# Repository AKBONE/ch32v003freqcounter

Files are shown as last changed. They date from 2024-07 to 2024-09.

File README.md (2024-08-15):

# ch32v003freqcounter

This is an electronic construction kit teaching material for kids' science experiment classes.
## Sound learning

It takes in sound, counts the frequencies, and displays them.

Learn what frequency various sounds are,
You can learn how the Doppler effect is generated by motion to a sound source.

In the future, the system will be able to display waveforms, measure ultrasonic frequencies, and output sounds of arbitrary frequencies.
This will allow students to learn that sound is a wave, that sounds are not audible to humans, and that different sounds can be heard at different ages.

## Concept
We try to make the kit as inexpensive as possible. We try to make the kit as inexpensive as possible and use inexpensive microcontrollers for this purpose.

## Soldering Training
The main components are soldered at the factory during manufacturing. The remaining few through-hole parts are made to be completed by soldering.

## Applications

With its small footprint and fast screen display, it can be used as a small signage.

# Circuit

## Schematic



## artdesign


# pin assign

| CH32V003F4P6 PIN |           | OLED PIN | OLED |
|------------------|-----------|----------|------|
|                  |           | 1        | GND  |
|                  |           | 2        | 3.3V |
| 15               |           | 3        | D0   |
| 16               | MOSI       | 4        | D1   |
| 17               | PC7(MISO) | 5        | RST  |
| 14               | PC4      | 6        | DC   |
| 13               | PC3       | 7        | CS   |

| CH32V003F4P6 PIN |       | PROGRAM PIN |   | LED(D1) |         |
|------------------|-------|-------------|-------|---------|---------|
|                  |       | 1           | 3.3V  |         |         |
| 18               | SWDIO | 2           | SWDIO |         |         |
|                  |       | 3           | GND   |         | CATHODE |
| 4                | NRST  | 4           | RST   |         |         |
| 2                | UTX   | 5           | TX    |         | ANODE   |
| 3                | URX   | 6           | RX    |         |         |

| CH32V003F4P6 PIN |           | SW  |  |
|------------------|-----------|-----|------|
| 8                | PD0       | SW1 | OK   |
| 10               | PC0       | SW2 | ↓    |
| 1                | PD4       | SW3 | ↑    |

| CH32V003F4P6 PIN |         | SEEED_GROVE |    |
|------------------|---------|-------------|--------|
| 12               | PC2/SCL | 1           | YELLOW |
| 11               | PC1/SDA | 2           | WHITE  |
|                  |         | 3           | 3.3V   |
|                  |         | 4           | GND    |

| CH32V003F4P6 PIN |        | NAX4466_MIC_MODULE |  |
|------------------|--------|--------------------|------|
| 20               | PD3/A4 | 1                  | OUT  |
|                  |        | 2                  | GND  |
|                  |        | 3                  | 3.3V |

| CH32V003F4P6 PIN |      | SPEAKER |  |
|------------------|------|---------|------|
|                  |      | 1       | GND  |
| 19               | PD2  | 2       | IN   |

## Links
- [ユーザ向けポータルサイト](https://akbone.github.io/ch32v003freqcounter/)
- [50円マイコン ch32v003 を使った簡単キット(AKBONE2024)を組み立てる #RISC-V - Qiita](https://qiita.com/nanbuwks/items/22680849ee7674d66a89)

### For Engineer
- [AKBONE/ch32v003freqcounter](https://github.com/AKBONE/ch32v003freqcounter)
- [cnlohr/ch32v003fun: Open source minimal stack for the ch32 line of WCH processors, including the ch32v003, a 10¢ 48 MHz RISC-V Microcontroller - as well as many other chips within the ch32v/x line.](https://github.com/cnlohr/ch32v003fun)

#### Parts
- [32ビットRISC-Vマイコン CH32V003F4P6: 半導体 秋月電子通商-電子部品・ネット通販](https://akizukidenshi.com/catalog/g/g118061/)
  - [データシート](https://akizukidenshi.com/goodsaffix/CH32V003.pdf)

# License

Public Domain ((cc0)
However, libraries used are subject to individual licenses.

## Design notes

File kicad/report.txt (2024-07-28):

情報: ファイル '/home/nanbuwks/00storage/KiCad/FreqCounter3203/github/kicad/sym-lib-table' をファイル '/home/nanbuwks/00storage/KiCad/FreqCounter3203/github/kicad/rescue-backup/sym-lib-table-2024-07-25-21-31-20' にバックアップしています。
情報: ファイル '/home/nanbuwks/00storage/KiCad/FreqCounter3203/github/kicad/FreqCounter3203.sch' をファイル '/home/nanbuwks/00storage/KiCad/FreqCounter3203/github/kicad/rescue-backup/FreqCounter3203-2024-07-25-21-31-20.sch' にバックアップしています。
情報: ファイル '/home/nanbuwks/00storage/KiCad/FreqCounter3203/github/kicad/FreqCounter3203.kicad_pro' をファイル '/home/nanbuwks/00storage/KiCad/FreqCounter3203/github/kicad/rescue-backup/FreqCounter3203-2024-07-25-21-31-20.kicad_pro' にバックアップしています。
情報: ファイル '/home/nanbuwks/00storage/KiCad/FreqCounter3203/github/kicad/FreqCounter3203-cache.lib' をファイル '/home/nanbuwks/00storage/KiCad/FreqCounter3203/github/kicad/rescue-backup/FreqCounter3203-cache-2024-07-25-21-31-20.lib' にバックアップしています。
情報: ファイル '/home/nanbuwks/00storage/KiCad/FreqCounter3203/github/kicad/FreqCounter3203-rescue.lib' をファイル '/home/nanbuwks/00storage/KiCad/FreqCounter3203/github/kicad/rescue-backup/FreqCounter3203-rescue-2024-07-25-21-31-20.lib' にバックアップしています。
情報: ファイル '/home/nanbuwks/00storage/KiCad/FreqCounter3203/github/kicad/FreqCounter3203-rescue.dcm' をファイル '/home/nanbuwks/00storage/KiCad/FreqCounter3203/github/kicad/rescue-backup/FreqCounter3203-rescue-2024-07-25-21-31-20.dcm' にバックアップしています。
情報: ライブラリ 'FreqCounter3203-rescue' , ファイル '${KIPRJMOD}/FreqCounter3203-rescue.lib' をプロジェクトのシンボル ライブラリ テーブルへ追加します。
シンボル 'CONN_01X06' はシンボル ライブラリ 'FreqCounter3203-rescue' にマップされました。
シンボル 'DIODESCH' はシンボル ライブラリ 'FreqCounter3203-rescue' にマップされました。
シンボル 'SWITCH_INV' はシンボル ライブラリ 'FreqCounter3203-rescue' にマップされました。
シンボル 'Battery' はシンボル ライブラリ 'FreqCounter3203-rescue' にマップされました。
シンボル 'CONN_02X03' はシンボル ライブラリ 'FreqCounter3203-rescue' にマップされました。
シンボル 'Battery' はシンボル ライブラリ 'FreqCounter3203-rescue' にマップされました。
シンボル 'SW_PUSH' はシンボル ライブラリ 'FreqCounter3203-rescue' にマップされました。
シンボル 'SW_PUSH' はシンボル ライブラリ 'FreqCounter3203-rescue' にマップされました。
シンボル 'C' はシンボル ライブラリ 'FreqCounter3203-rescue' にマップされました。
シンボル 'PhotoReciever_GP1USC4XQS_SHARP' はシンボル ライブラリ 'FreqCounter3203-rescue' にマップされました。
シンボル 'GND' はシンボル ライブラリ 'FreqCounter3203-rescue' にマップされました。
シンボル 'R' はシンボル ライブラリ 'FreqCounter3203-rescue' にマップされました。
シンボル 'SW_PUSH' はシンボル ライブラリ 'FreqCounter3203-rescue' にマップされました。
シンボル 'SW_PUSH' はシンボル ライブラリ 'FreqCounter3203-rescue' にマップされました。
シンボル '+3.3V' はシンボル ライブラリ 'FreqCounter3203-rescue' にマップされました。
シンボル 'R' はシンボル ライブラリ 'FreqCounter3203-rescue' にマップされました。
シンボル 'GND' はシンボル ライブラリ 'FreqCounter3203-rescue' にマップされました。
シンボル 'GND' はシンボル ライブラリ 'FreqCounter3203-rescue' にマップされました。
シンボル '+3.3V' はシンボル ライブラリ 'FreqCounter3203-rescue' にマップされました。
シンボル 'STM32F103C8T6MinimumDevelopBoard-RESCUE-nodrinknohack' はシンボル ライブラリ 'FreqCounter3203-rescue' にマップされました。
シンボル 'SPEAKER' はシンボル ライブラリ 'FreqCounter3203-rescue' にマップされました。
シンボル 'GND' はシンボル ライブラリ 'FreqCounter3203-rescue' にマップされました。
シンボル 'SW_PUSH' はシンボル ライブラリ 'FreqCounter3203-rescue' にマップされました。
シンボル 'GND' はシンボル ライブラリ 'FreqCounter3203-rescue' にマップされました。
シンボル '+3.3V' はシンボル ライブラリ 'FreqCounter3203-rescue' にマップされました。
シンボル 'OLED_0.96in_SPI' はシンボル ライブラリ 'FreqCounter3203-rescue' にマップされました。
シンボル 'R' はシンボル ライブラリ 'FreqCounter3203-rescue' にマップされました。
シンボル 'LED' はシンボル ライブラリ 'FreqCounter3203-rescue' にマップされました。
シンボル 'GND' はシンボル ライブラリ 'FreqCounter3203-rescue' にマップされました。
シンボル 'SW_PUSH' はシンボル ライブラリ 'FreqCounter3203-rescue' にマップされました。
シンボル 'R' はシンボル ライブラリ 'FreqCounter3203-rescue' にマップされました。
シンボル '+3.3V' はシンボル ライブラリ 'FreqCounter3203-rescue' にマップされました。
情報: シンボル ライブラリ テーブルのマッピングを完了!
情報: プロジェクトのシンボル ライブラリ テーブルを作成しました。

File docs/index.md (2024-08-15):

# AKBONE2024 (ch32v003freqcounter)

「おとカウンター」キットのページです。
いろんなイベントで頒布しています。

## 教科書

最新の教科書はこちら
-  [textbook](./text/textbook.pdf) 

過去の教科書は「イベント」内のリンクを参照してください。

## こんなときは

### 使い方を知りたい

「イベント」内に、イベントで頒布したキットの説明書のリンクがあります。説明書で確認してください。

### こわれちゃったよ!

「OpenHardTerrace」という Discord サーバでサポートしています。

[https://discord.gg/9UTNdtSrdX](https://discord.gg/9UTNdtSrdXa)

こちらに参加後、ご連絡ください。

あらかじめ、 Discord のアカウントの用意が必要です。 
ご参加後、 「PROJECTS」 →  「akbone2024」 に行き、いつどこで入手したかと症状を書いてください。

Discord へのアクセスが難しい場合は、以下の住所まではがきでご連絡ください。

〒297-0037 千葉県茂原市早野2756-2
秘密結社オープンフォース 秘密基地

### より知りたいとき

技術的な設計情報などは、 GitHub で管理しています。
[https://github.com/AKBONE/ch32v003freqcounter](https://github.com/AKBONE/ch32v003freqcounter)
また、「こわれちゃったよ」と同じ Discord サーバーで開発をしています。興味があればご参加ください。

## イベント
- 2024/08/04 [なつやすみこども科学実験教室2024](./events/2024-08-04/) @東京都足立区伊興地域学習センター [https://openforce.connpass.com/event/326569/](https://openforce.connpass.com/event/326569/)
- 2024/08/10 [なつやすみこども科学実験教室2024](./events/2024-08-10-11/) @石川県七尾市和倉地区コミュニティセンター
- 2024/08/11 [なつやすみ科学実験教室2024](./events/2024-08-10-11/) @石川県珠洲市旧正院保育所

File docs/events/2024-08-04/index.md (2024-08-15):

# 2024-08-04

東京都足立区伊興コミュニティセンターで開催した科学実験教室内で「おとカウンターをはんだづけしてみよう！」コーナーとして頒布しました。

## 説明書
[https://docs.google.com/document/d/1sSZhSKSC-4plJ0KE5L4aG0ssfCy5kGWXfLFpL6DbHqM/](https://docs.google.com/document/d/1sSZhSKSC-4plJ0KE5L4aG0ssfCy5kGWXfLFpL6DbHqM/)
## イベントサイト 
- [なつやすみこども科学実験教室2024 - connpass](https://openforce.connpass.com/event/326569/)

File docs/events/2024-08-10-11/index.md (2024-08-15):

# 2024/08/10-11

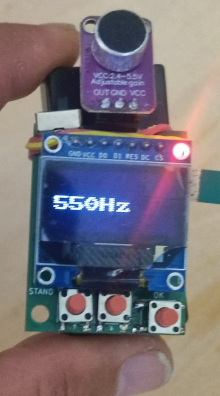
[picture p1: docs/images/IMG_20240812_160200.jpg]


## 開催

### 2024/08/10

- 2024/08/10 なつやすみこども科学実験教室2024 @石川県七尾市和倉地区コミュニティセンター
- 2024/08/11 なつやすみ科学実験教室2024 @石川県珠洲市旧正院保育所

## テキストブック
-  [textbook](./text/textbook.pdf)

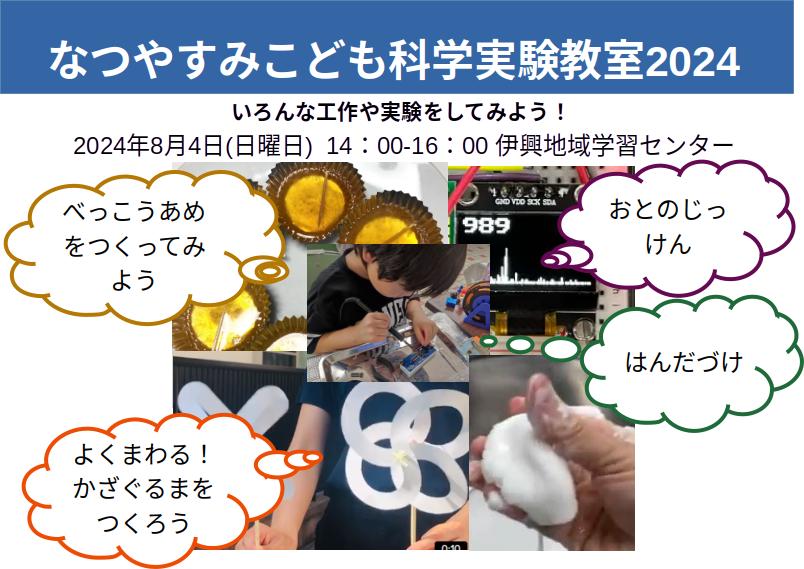
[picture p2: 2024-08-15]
pictures/leaflets.jpg

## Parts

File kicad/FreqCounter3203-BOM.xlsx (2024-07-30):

Comment | Designator | Footprint
2.7kΩ | R2 | R_0603_1608Metric | C13167
47 | R9,R8 | R_0603_1608Metric | C23179
1u | C6 | C_0603_1608Metric | C59302
20p | C2,C3 | C_0603_1608Metric | C165732
10u | C4,C5 | C_0603_1608Metric | C38898
0.1u | C1 | C_0603_1608Metric | C14663
XC6206PxxxMR | U4 | SOT-23-3 | C5446
5.1k | R5,R6 | R_0603_1608Metric | c23186
TACTSWWITCH | SW1,SW2,SW3 | SW_Push_1P1T_NO_6x6mm_H9.5mm | c2837533
180Ω | R1 | R_0603_1608Metric | c22828
CH32V003F4P6 | U3 | TSSOP-20_4.4x6.5mm_P0.65mm | c5187096
1.5k | R7 | R_0603_1608Metric | c22843
USB-C_16PIN | U5 | USB_Type_C_16Pin_Female | c393939
Battery | BT1 | BatteryHolder_Keystone_3002_1x2032 | c964834
LED | D1 | LED_D3.0mm | C2895470
SEEED_GROVE | U1 | JST_PH_B4B-PH-K_1x04_P2.00mm_Vertical | C722737

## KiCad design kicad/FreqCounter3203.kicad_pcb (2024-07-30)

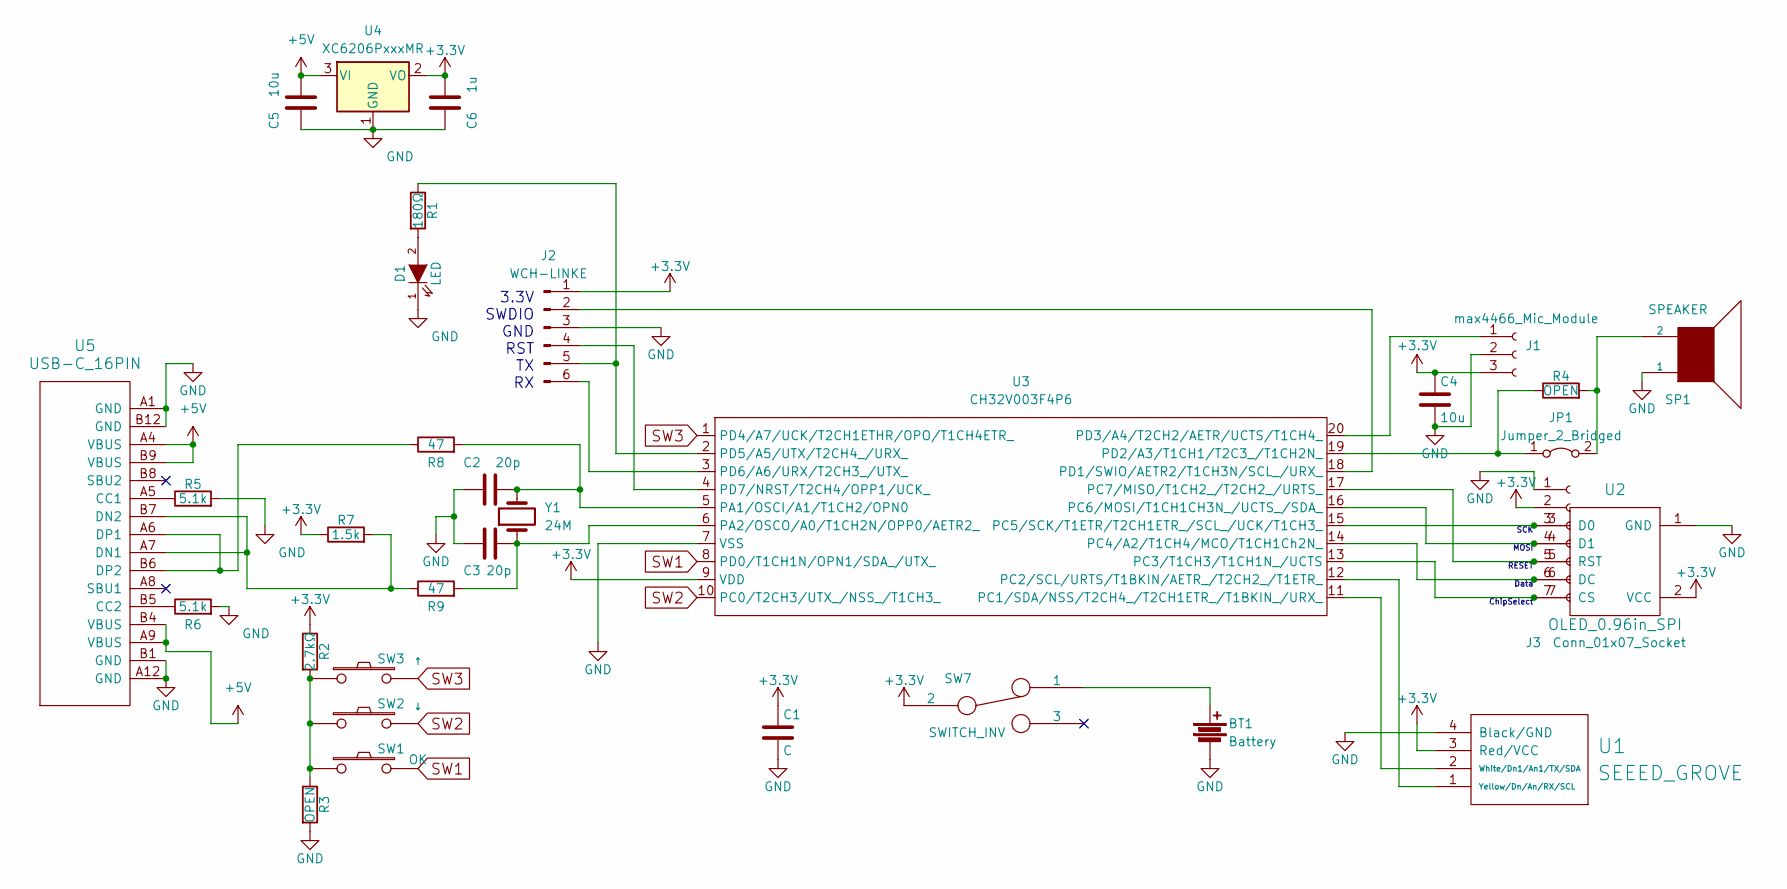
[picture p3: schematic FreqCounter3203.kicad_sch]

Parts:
BT1: Battery; BatteryHolder_Keystone_3002_1x2032
C1: C; C_0603_1608Metric
C2, C3: 20p; C_0603_1608Metric
C4, C5: 10u; C_0603_1608Metric
C6: 1u; C_0603_1608Metric
D1: LED; LED_D3.0mm
J1: max4466_Mic_Module; PinHeader_1x03_P2.54mm_Vertical
J2: WCH-LINKE; PinHeader_1x06_P2.54mm_Vertical
J3: Conn_01x07_Socket; PinSocket_1x07_P2.54mm_Vertical
JP1: Jumper_2_Bridged; SolderJumper-2_P1.3mm_Bridged_Pad1.0x1.5mm
R1: 180Ω; R_0603_1608Metric
R2: 2.7kΩ; R_0603_1608Metric
R3, R4: OPEN; R_0603_1608Metric
R5, R6: 5.1k; R_0603_1608Metric
R7: 1.5k; R_0603_1608Metric
R8, R9: 47; R_0603_1608Metric
SP1: SPEAKER; Buzzer_TDK_PS1240P02BT_D12.2mm_H6.5mm
SW1: OK; SW_Push_1P1T_NO_6x6mm_H9.5mm
SW2: ↓; SW_Push_1P1T_NO_6x6mm_H9.5mm
SW3: ↑; SW_Push_1P1T_NO_6x6mm_H9.5mm
SW7: SWITCH_INV; PinHeader_1x03_P2.54mm_Vertical
U1: SEEED_GROVE; JST_PH_B4B-PH-K_1x04_P2.00mm_Vertical
U2: OLED_0.96in_SPI
U3: CH32V003F4P6; TSSOP-20_4.4x6.5mm_P0.65mm
U4: XC6206PxxxMR; SOT-23-3
U5: USB-C_16PIN; USB_Type_C_16Pin_Female
Y1: 24M; Crystal_SMD_HC49-SD

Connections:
+3V3: C1.1, C4.1, C6.2, J1.3, J2.1, J3.2, R2.1, R7.1, SW7.2, U1.3 (Red/VCC), U2.2 (VCC), U3.9 (VDD), U4.2 (VO)
+5V: C5.2, U4.3 (VI), U5.A4 (VBUS), U5.A9 (VBUS), U5.B4 (VBUS), U5.B9 (VBUS)
GND: BT1.2, C1.2, C2.1, C3.1, C4.2, C5.1, C6.1, D1.1 (K), J1.2, J2.3, J3.1, R3.2, R5.2, R6.2, SP1.1, U1.4 (Black/GND), U2.1 (GND), U3.7 (VSS), U4.1 (GND), U5.A1 (GND), U5.A12 (GND), U5.B1 (GND), U5.B12 (GND)
unnamed: BT1.1, SW7.1
unnamed: D1.2 (A), R1.2
unnamed: J1.1, U3.20 (PD3/A4/T2CH2/AETR/UCTS/T1CH4_)
unnamed: J2.2, U3.18 (PD1/SWIO/AETR2/T1CH3N/SCL_/URX_)
unnamed: J2.4, U3.4 (PD7/NRST/T2CH4/OPP1/UCK_)
unnamed: J2.5, R1.1, U3.2 (PD5/A5/UTX/T2CH4_/URX_)
unnamed: J2.6, U3.3 (PD6/A6/URX/T2CH3_/UTX_)
unnamed: J3.3, U2.3 (D0), U3.15 (PC5/SCK/T1ETR/T2CH1ETR_/SCL_/UCK/T1CH3_)
unnamed: J3.4, U2.4 (D1), U3.16 (PC6/MOSI/T1CH1CH3N_/UCTS_/SDA_)
unnamed: J3.5, U2.5 (RST), U3.17 (PC7/MISO/T1CH2_/T2CH2_/URTS_)
unnamed: J3.6, U2.6 (DC), U3.14 (PC4/A2/T1CH4/MCO/T1CH1Ch2N_)
unnamed: J3.7, U2.7 (CS), U3.13 (PC3/T1CH3/T1CH1N_/UCTS)
unnamed: JP1.1 (A), R4.1, U3.19 (PD2/A3/T1CH1/T2C3_/T1CH2N_)
unnamed: JP1.2 (B), R4.2, SP1.2
unnamed: R2.2, R3.1, SW1.1, SW2.1, SW3.1
unnamed: U1.2 (White/Dn1/An1/TX/SDA), U3.11 (PC1/SDA/NSS/T2CH4_/T2CH1ETR_/T1BKIN_/UR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)
unnamed: U1.1 (Yellow/Dn/An/RX/SCL), U3.12 (PC2/SCL/URTS/T1BKIN/AETR_/T2CH2_/T1ETR_)
unnamed: C2.2, R8.2, U3.5 (PA1/OSCI/A1/T1CH2/OPN0), Y1.2
unnamed: C3.2, R9.2, U3.6 (PA2/OSCO/A0/T1CH2N/OPP0/AETR2_), Y1.1
unnamed: R5.1, U5.A5 (CC1)
unnamed: R6.1, U5.B5 (CC2)
unnamed: R7.2, R9.1, U5.A7 (DN1), U5.B7 (DN2)
unnamed: R8.1, U5.A6 (DP1), U5.B6 (DP2)
SW1: SW1.2, U3.8 (PD0/T1CH1N/OPN1/SDA_/UTX_)
SW2: SW2.2, U3.10 (PC0/T2CH3/UTX_/NSS_/T1CH3_)
SW3: SW3.2, U3.1 (PD4/A7/UCK/T2CH1ETHR/OPO/T1CH4ETR_)

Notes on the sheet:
3.3V SWDIO GND RST TX RX
SCK MOSI RESET Data ChipSelect

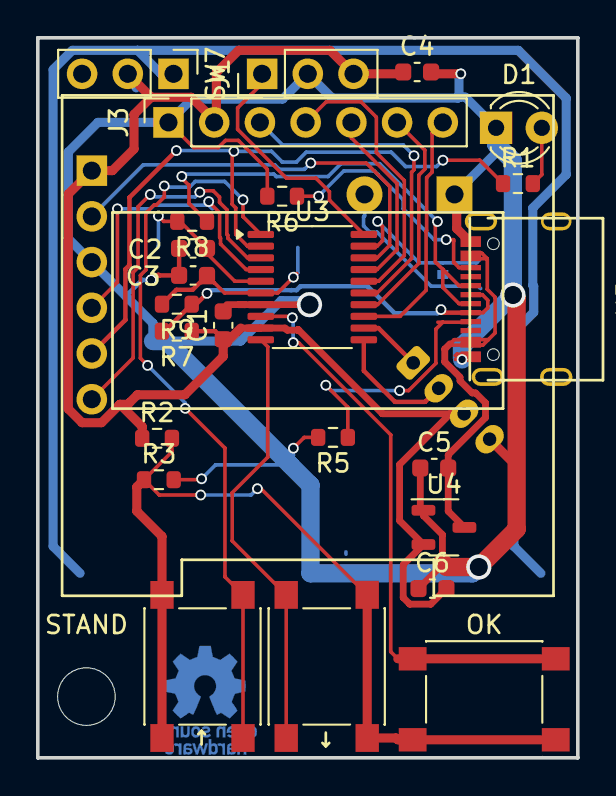
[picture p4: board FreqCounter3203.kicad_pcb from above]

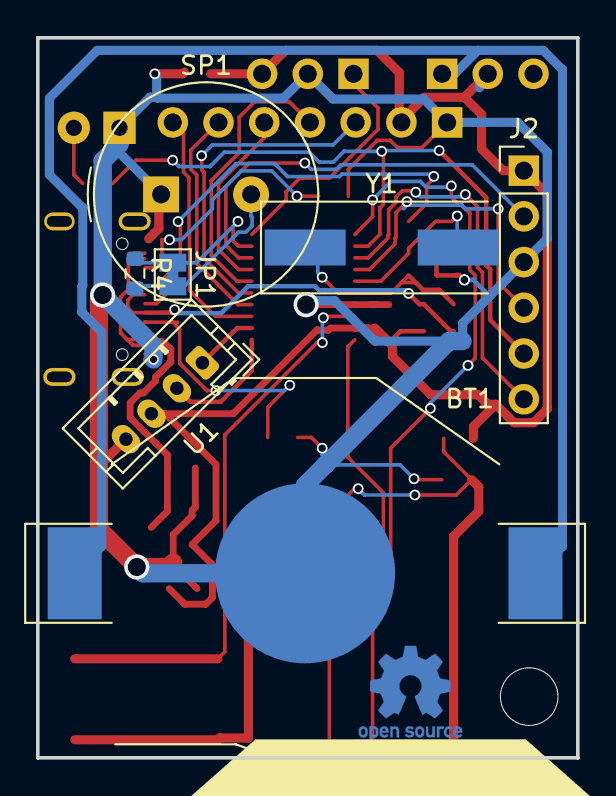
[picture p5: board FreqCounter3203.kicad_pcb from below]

Board: 2 copper layers, 30.0 x 40.0 mm, 32 parts (7 on the bottom side), 29 nets.

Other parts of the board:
STAND: MountingHole_3mm

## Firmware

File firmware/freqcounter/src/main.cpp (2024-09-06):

//
//	freqcounter Ver 1.1.1
//
//  2024.07.31 New Create
//
#include <stdio.h>
#include <stdlib.h> 
#include <math.h>
#include "fix_fft.h"
#include "ch32v003fun.h"

#define micros() (SysTick->CNT / DELAY_US_TIME)
#define millis() (SysTick->CNT / DELAY_MS_TIME)

// what type of OLED - uncomment just one
//#define SSD1306_64X32
//#define SSD1306_128X32
#define SSD1306_128X64
#define SCALE 3

#define GPIO_ADC_MUX_DELAY 100
#define GPIO_ADC_sampletime GPIO_ADC_sampletime_43cy
#include "ch32v003_GPIO_branchless.h"
#include "ssd1306_spi.h"
#include "ssd1306.h"

#define LED_PIN GPIOv_from_PORT_PIN(GPIO_port_D, 5)
#define SW1_PIN GPIOv_from_PORT_PIN(GPIO_port_D, 0)
#define SW2_PIN GPIOv_from_PORT_PIN(GPIO_port_D, 4)
#define SW3_PIN GPIOv_from_PORT_PIN(GPIO_port_C, 0)
#define ADC_PIN GPIOv_from_PORT_PIN(GPIO_port_D, 3)
#define SPK_PIN GPIOv_from_PORT_PIN(GPIO_port_D, 2)

#define SAMPLES 256 // 2の累乗である必要があります
#define SAMPLING_FREQUENCY 6000

uint16_t sampling_period_us;
int8_t vReal[SAMPLES];
int8_t vImag[SAMPLES];

#include "qr.h"

// function prototype (declaration), definition in "ch32v003fun.c"
extern "C" int mini_snprintf(char* buffer, unsigned int buffer_len, const char *fmt, ...);
char title1[] = "FrequencyCounter";
char title2[] = "  Version 1.1.1 ";


void setup()
{
    // 各GPIOの有効化
    GPIO_port_enable(GPIO_port_D);
    GPIO_port_enable(GPIO_port_C);
    // 各ピンの設定
    GPIO_pinMode(SW1_PIN, GPIO_pinMode_I_pullDown, GPIO_Speed_10MHz); /// GPIO_Speed_In? @see https://github.com/cnlohr/ch32v003fun/blob/master/examples/GPIO/GPIO.c#L55
    GPIO_pinMode(SW2_PIN, GPIO_pinMode_I_pullDown, GPIO_Speed_10MHz);
    GPIO_pinMode(SW3_PIN, GPIO_pinMode_I_pullDown, GPIO_Speed_10MHz);

	ssd1306_spi_init();		// i2c Setup
	ssd1306_init();			// SSD1306 Setup
	ssd1306_setbuf(0);		// Clear Screen
	ssd1306_drawstr_sz(0, 24, title1, 1, fontsize_8x8);
	ssd1306_drawstr_sz(0, 40, title2, 1, fontsize_8x8);
	ssd1306_refresh();
}

// void alertNotImpl() {
// 	ssd1306_setbuf(0);		// Clear Screen
// 	ssd1306_drawstr_sz(0, 24, "      Not       ", 1, fontsize_8x8);
// 	ssd1306_drawstr_sz(0, 40, "  Implemented!  ", 1, fontsize_8x8);
// 	ssd1306_refresh();
// 	Delay_Ms(1000);
// }

// void alertDefaultError() {
// 	ssd1306_setbuf(0);		// Clear Screen
// 	ssd1306_drawstr_sz(0, 24, "some error occurrs", 1, fontsize_8x8);
// 	ssd1306_drawstr_sz(0, 40, "    Reboot Me!    ", 1, fontsize_8x8);
// 	ssd1306_refresh();
// 	while(1);
// }

void drawIcon(uint8_t *data, uint8_t size, uint8_t x_base, uint8_t y_base, uint8_t color) {
	for (uint8_t i = 0; i < size; i++) {
		for (uint8_t j = 0; j < size; j++) {
			uint8_t pixel = *(data + i * size + j);
			bool _color = (color && pixel) || (!color && !pixel);
			ssd1306_drawPixel(x_base + j, y_base + i, _color);
		}
	}
}

void drawWaveIcon0(uint8_t x_base, uint8_t y_base, uint8_t color) {
	uint8_t data[8][8] = {
		{0, 0, 0, 0, 1, 0, 0, 0},
		{0, 0, 0, 1, 0, 1, 0, 0},
		{0, 0, 1, 0, 0, 0, 1, 0},
		{0, 0, 1, 0, 0, 0, 1, 0},
		{0, 1, 0, 0, 0, 0, 0, 1},
		{0, 1, 0, 0, 0, 0, 0, 1},
		{1, 0, 0, 0, 0, 0, 0, 0},
		{1, 0, 0, 0, 0, 0, 0, 0},
	};

	drawIcon((uint8_t*) data, 8, x_base, y_base, color);
}

void drawWaveIcon1(uint8_t x_base, uint8_t y_base, uint8_t color) {
	uint8_t data[8][8] = {
		{1, 0, 0, 0, 0, 0, 0, 0},
		{1, 0, 0, 0, 0, 0, 0, 0},
		{0, 1, 0, 0, 0, 0, 0, 1},
		{0, 1, 0, 0, 0, 0, 0, 1},
		{0, 0, 1, 0, 0, 0, 1, 0},
		{0, 0, 1, 0, 0, 0, 1, 0},
		{0, 0, 0, 1, 0, 1, 0, 0},
		{0, 0, 0, 0, 1, 0, 0, 0},
	};

	drawIcon((uint8_t*) data, 8, x_base, y_base, color);
}

void drawNoteIcon(uint8_t x_base, uint8_t y_base, uint8_t color) {
	uint8_t data[8][8] = {
		{0, 0, 0, 0, 1, 0, 0, 0},
		{0, 0, 0, 0, 1, 1, 0, 0},
		{0, 0, 0, 0, 1, 1, 1, 0},
		{0, 0, 0, 0, 1, 0, 1, 1},
		{0, 0, 0, 0, 1, 0, 0, 0},
		{0, 0, 1, 1, 1, 0, 0, 0},
		{0, 1, 1, 1, 1, 0, 0, 0},
		{0, 0, 1, 1, 0, 0, 0, 0},
	};

	drawIcon((uint8_t*) data, 8, x_base, y_base, color);
}

uint8_t showInitMenu() {
	uint8_t mode = 0;

	while(1) {
		ssd1306_setbuf(0);	// Clear Screen
		ssd1306_drawstr_sz(0, 0, "30-3000Hz", !(mode == 0), fontsize_8x8);

		/**
		 * ~ (Real time)
		 * margin-top = 3 = floor(((26 - 5) - (16 - 2)) / 2)
		 */
		ssd1306_fillRect(0, (13 + 3), 8 * 4, (8 - 1) * 2, mode == 1);
		drawWaveIcon0(0, (13 + 3), !(mode == 1));
		drawWaveIcon1(8, (13 + 3) + 8 - 2, !(mode == 1));
		drawWaveIcon0(16, (13 + 3), !(mode == 1));
		drawWaveIcon1(24, (13 + 3) + 8 - 2, !(mode == 1));

		drawNoteIcon(0, 39, !(mode == 2)); /// ♪
		// ssd1306_drawstr_sz(0, 13, "900-1100Hz", !(mode == 3), fontsize_8x8);
		ssd1306_drawstr_sz(0, 52, "QR code", !(mode == 3), fontsize_8x8);
		ssd1306_refresh();

		if (GPIO_digitalRead(SW1_PIN)) {
			// printf("SW1: OK\n");
			switch (mode)
			{
				case 0:
				case 1:
				case 2:
				case 3:
					Delay_Ms(300);
					return mode;
				default:
					// alertNotImpl();
				break;
			}
		}

		if (GPIO_digitalRead(SW2_PIN)) {
			// printf("SW2: Up\n");
			Delay_Ms(100);
			if (mode <= 0) {
				mode = 3;
			} else {
				mode--;
			}
		}

		if (GPIO_digitalRead(SW3_PIN)) {
			// printf("SW3: Down\n");
			Delay_Ms(100);
			if (mode >= 3) {
				mode = 0;
			} else {
				mode++;
			}
		}
		Delay_Ms(100);
	}
}

void setupModeFreqCounter0()
{
    // 各GPIOの有効化
    GPIO_port_enable(GPIO_port_D);
    // 各ピンの設定
    GPIO_pinMode(ADC_PIN, GPIO_pinMode_I_analog, GPIO_Speed_10MHz);
	GPIO_ADCinit();
	sampling_period_us = 1000000 / SAMPLING_FREQUENCY;
}

int loopModeFreqCounter0() {
	char buf[16];

	while(1) {
		uint16_t ave = 0;
		uint8_t  val = 0;
		ssd1306_setbuf(0);	// Clear Screen
		for (int i = 0; i < SAMPLES; i++) {
			unsigned long t = micros();
			val = (uint8_t)(GPIO_analogRead(GPIO_Ain4_D3) >> 2);
			ave += val;
			vImag[i] = val;
			while ((micros() - t) < sampling_period_us);
		}
		ave = ave / SAMPLES;
		//printf("ave = %d\n", ave);
		for (int i = 0; i < SAMPLES; i++) {
			vReal[i] = (int8_t)(vImag[i] - ave);
			vImag[i] = 0; // Imaginary partは0に初期化
		}

  		fix_fft((char *)vReal, (char *)vImag, 8, 0); // SAMPLES = 32なので、log2(SAMPLES) = 5

  		/* Magnitude Calculation */
		for (int i = 0; i < SAMPLES / 2; i++) {
			vReal[i] = abs(vReal[i]) + abs(vImag[i]); // Magnitude calculation without sqrt
			//vReal[i] = sqrt(vReal[i] * vReal[i] + vImag[i] * vImag[i]);
		}
		/* Find Peak */
		uint8_t maxIndex = 0;
		uint8_t maxValue = 0;
		for (int i = 8; i < SAMPLES / 2; i++) {
			int8_t val = (vReal[i] * SCALE < 48) ? vReal[i] * SCALE : 48;  
			ssd1306_drawFastVLine(i, 63 - val + 1, val + 1, 1);
			if (vReal[i] > maxValue) {
				maxValue = vReal[i];
				maxIndex = i;
			}
		}
		// disp freqeuncy
		int peakFrequency = (SAMPLING_FREQUENCY / SAMPLES) * maxIndex;
 		if (maxValue >= 4 ) {
//			uint16_to_string(peakFrequency + 12, buf, sizeof(buf));
			mini_snprintf(buf, sizeof(buf), " %4dHz", peakFrequency + 12);
		    //printf("%d\n", peakFrequency); // Print out what frequency is the most dominant.
  		} else {
			strcpy(buf, "    0Hz");
		}
//		strcat(buf, "Hz");
		ssd1306_drawstr_sz((6 - strlen(buf)) * 16 + 16, 1, buf, 1, fontsize_16x16);
		ssd1306_drawFastHLine(  0,   0,  128, 1);
		ssd1306_drawFastHLine(  0,  16,  128, 1);
		ssd1306_drawFastHLine(  0,  63,  128, 1);
		ssd1306_drawFastVLine(  0,   0,   64, 1);
		ssd1306_drawFastVLine(127,   0,   64, 2);

		ssd1306_refresh();
	}
}

void setupModeTone()
{
    // 各GPIOの有効化
    GPIO_port_enable(GPIO_port_D);
    // 各ピンの設定
    GPIO_pinMode(LED_PIN, GPIO_pinMode_O_pushPull, GPIO_Speed_10MHz);
    GPIO_pinMode(SPK_PIN, GPIO_pinMode_O_pushPull, GPIO_Speed_10MHz);
}

void displayModeTone(uint16_t f) {
	char buf[16];

	if (f) {
		mini_snprintf(buf, sizeof(buf), "%dHz",  f);
	} else {
		mini_snprintf(buf, sizeof(buf), "Mute");
	}
	ssd1306_setbuf(0);	// Clear Screen
	// ssd1306_drawstr_sz((6 - strlen(buf)) * 16 + 16, 1, buf, 1, fontsize_16x16);
	ssd1306_drawstr_sz(0, 28, buf, 1, fontsize_16x16);
	ssd1306_refresh();
}

int loopModeTone() {
	int32_t midiNoteNum;
	uint16_t f;
	uint16_t delay;
	bool dirty;

	midiNoteNum = 69;
	f = 440;

	delay = (1000 * 1000) / (2 * f);
	dirty = false;

	displayModeTone(f);

	while(1) {
		if (dirty) {
			dirty = false;

			if (midiNoteNum > 69) {
//				f = 440 * (1 + (midiNoteNum - 69) / 12);
				f = 440 + (440 * midiNoteNum - 69 * 440) / 12;
			} else if (midiNoteNum < 69) {
//				f = 440 / (1 - (midiNoteNum - 69) / 12);
				f = 5280 / (81 - midiNoteNum);
			} else {
				f = 440;
			}

			// f = 440.0 * pow(2.0, (midiNoteNum - 69) / 12.0);

			displayModeTone(f);
			// printf("%d\n", midiNoteNum);

			delay = (1000 * 1000) / (2 * f);
		}

		GPIO_digitalWrite(LED_PIN, high);
		GPIO_digitalWrite(SPK_PIN, high);
		Delay_Us(delay);
		GPIO_digitalWrite(LED_PIN, low);
		GPIO_digitalWrite(SPK_PIN, low);
		Delay_Us(delay);

		if (GPIO_digitalRead(SW1_PIN)) {
			// printf("SW1: OK\n");
			displayModeTone(0);
			Delay_Ms(300);

			while(!GPIO_digitalRead(SW1_PIN));

			displayModeTone(f);
			Delay_Ms(300);
		}

		if (GPIO_digitalRead(SW2_PIN)) {
			// printf("SW2: Up\n");
			if (midiNoteNum >= INT32_MAX) {
				;
			} else if (midiNoteNum < 0) {
				midiNoteNum /= 2;
			} else {
				midiNoteNum++;
			}
			dirty = true;
			Delay_Ms(100);
		}

		if (GPIO_digitalRead(SW3_PIN)) {
			// printf("SW3: Down\n");
			if (midiNoteNum <= -1024) { /// 周波数が 2 以下にならないように制御
				;
			} else if (midiNoteNum < 0) {
				midiNoteNum *= 2;
			} else {
				midiNoteNum--;
			}
			dirty = true;
			Delay_Ms(100);
		}
	}
}

void setupModeRealtime()
{
	// 各GPIOの有効化
	GPIO_port_enable(GPIO_port_D);
	// 各ピンの設定
	GPIO_pinMode(ADC_PIN, GPIO_pinMode_I_analog, GPIO_Speed_10MHz);
	GPIO_ADCinit();
	sampling_period_us = 1000000 / SAMPLING_FREQUENCY;
}

int loopModeRealtime() {
	char buf[16];
//	uint16_t vals[128];
	uint16_t *vals;
	unsigned long t;

	uint8_t mode;
	uint32_t wait;
	uint32_t dt;

	vals = (uint16_t *)vReal;			// use vReal 
	mode = 0;
	wait = 100;
	dt = 0;

	t = millis();

	while(1) {
		if ((millis() - t) > wait) {
			t = millis();
			ssd1306_setbuf(0);	// Clear Screen

			if (dt) {
				for (int i = 0; i < 128; i++) {
					Delay_Us(dt);
					vals[i] = GPIO_analogRead(GPIO_Ain4_D3);
				}
			} else {
				for (int i = 0; i < 128; i++) {
					vals[i] = GPIO_analogRead(GPIO_Ain4_D3);
				}
			}

			for (int i = 0; i < 128; i++) {
				// val /= (int) ceil((max + 1) / 48.0);
				// val = floor(val / (max / 48.0));
				vals[i] = (int) (vals[i] / (1023 / 48)); /// MIC OUT is 0-1023
				vals[i] = (vals[i] < 48) ? vals[i] : 48;
				ssd1306_drawPixel(i, 63 - vals[i] + 1, 1);
			}
		}

		ssd1306_drawstr_sz(0, 0, "                ", 1, fontsize_8x8);

		switch (mode)
		{
			case 0: // wait
				mini_snprintf(buf, sizeof(buf), "wait: %u ms", wait);
			break;

			case 1: // dt
				mini_snprintf(buf, sizeof(buf), "dt: %u us", dt);
			break;
		}

		ssd1306_drawstr_sz(0, 0, buf, 1, fontsize_8x8);
		// ssd1306_drawFastHLine(0, 40, 127, 1); /// y = 40 = (64 - 16) / 2 + 16
		ssd1306_refresh();

		if (GPIO_digitalRead(SW1_PIN)) {
			// printf("SW1: OK\n");
			mode = (mode + 1) % 2;
			Delay_Ms(300);
		}

		if (GPIO_digitalRead(SW3_PIN)) {
			// printf("SW2: Up\n");
			switch (mode)
			{
				case 0: // wait
					wait += 10;
				break;

				case 1: // dt
					dt += 10;
				break;
			}
			Delay_Ms(200);
		}

		if (GPIO_digitalRead(SW2_PIN)) {
			// printf("SW3: Down\n");
			switch (mode)
			{
				case 0: // wait
					if (wait > (0 + 10)) {
						wait -= 10;
					} else {
						wait = 0;
					}
				break;

				case 1: // dt
					if (dt > (0 + 10))  {
						dt -= 10;
					} else {
						dt = 0;
					}
				break;
			}
			Delay_Ms(200);
		}
	}
}

int loopModeQrCode() {
	uint8_t color;

	color = 0;

	while(1) {
		ssd1306_setbuf(0);	// Clear Screen
		ssd1306_drawImage((128 - QR_WIDTH) / 2 - 8, (64 - QR_HEIGHT) / 2, qr_data, QR_WIDTH, QR_HEIGHT, color);
		ssd1306_refresh();

		if (GPIO_digitalRead(SW1_PIN)) {
			Delay_Ms(300);
			return 0;
		}

		if (GPIO_digitalRead(SW2_PIN) || GPIO_digitalRead(SW3_PIN)) {
			color = (color + 1) % 2;
			Delay_Ms(300);
		}
	}
}
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

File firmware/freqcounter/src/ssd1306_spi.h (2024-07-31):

/*
 * Single-File-Header for SSD1306 SPI interface
 * 05-05-2023 E. Brombaugh
 */

#ifndef _SSD1306_SPI_H
#define _SSD1306_SPI_H

// control pins
#define SSD1306_RST_PORT GPIOC
#define SSD1306_RST_PIN 7				// change 2 -> 7  for kawano board
#define SSD1306_RST_HIGH() SSD1306_RST_PORT->BSHR = (1<<(SSD1306_RST_PIN))
#define SSD1306_RST_LOW() SSD1306_RST_PORT->BSHR = (1<<(16+SSD1306_RST_PIN))
#define SSD1306_CS_PORT GPIOC
#define SSD1306_CS_PIN 3
#define SSD1306_CS_HIGH() SSD1306_CS_PORT->BSHR = (1<<(SSD1306_CS_PIN))
#define SSD1306_CS_LOW() SSD1306_CS_PORT->BSHR = (1<<(16+SSD1306_CS_PIN))
#define SSD1306_DC_PIN 4
#define SSD1306_DC_PORT GPIOC
#define SSD1306_DC_HIGH() SSD1306_DC_PORT->BSHR = (1<<(SSD1306_DC_PIN))
#define SSD1306_DC_LOW() SSD1306_DC_PORT->BSHR = (1<<(16+SSD1306_DC_PIN))

/*
 * init SPI and GPIO for SSD1306 OLED
 */
uint8_t ssd1306_spi_init(void)
{
	// Enable GPIOC and SPI
	RCC->APB2PCENR |= RCC_APB2Periph_GPIOC | RCC_APB2Periph_SPI1;
	
	// setup GPIO for reset, chip select and data/cmd
	SSD1306_RST_PORT->CFGLR &= ~(0xf<<(4*SSD1306_RST_PIN));
	SSD1306_RST_PORT->CFGLR |= (GPIO_Speed_10MHz | GPIO_CNF_OUT_PP)<<(4*SSD1306_RST_PIN);
	SSD1306_RST_HIGH();
	SSD1306_CS_PORT->CFGLR &= ~(0xf<<(4*SSD1306_CS_PIN));
	SSD1306_CS_PORT->CFGLR |= (GPIO_Speed_10MHz | GPIO_CNF_OUT_PP)<<(4*SSD1306_CS_PIN);
	SSD1306_CS_HIGH();
	SSD1306_DC_PORT->CFGLR &= ~(0xf<<(4*SSD1306_DC_PIN));
	SSD1306_DC_PORT->CFGLR |= (GPIO_Speed_10MHz | GPIO_CNF_OUT_PP)<<(4*SSD1306_DC_PIN);
	SSD1306_DC_LOW();

	// PC5 is SCK, 10MHz Output, alt func, p-p
	GPIOC->CFGLR &= ~(0xf<<(4*5));
	GPIOC->CFGLR |= (GPIO_Speed_10MHz | GPIO_CNF_OUT_PP_AF)<<(4*5);
	
	// PC6 is MOSI, 10MHz Output, alt func, p-p
	GPIOC->CFGLR &= ~(0xf<<(4*6));
	GPIOC->CFGLR |= (GPIO_Speed_10MHz | GPIO_CNF_OUT_PP_AF)<<(4*6);
	
	// Configure SPI 
	SPI1->CTLR1 = 
		SPI_NSS_Soft | SPI_CPHA_1Edge | SPI_CPOL_Low | SPI_DataSize_8b |
		SPI_Mode_Master | SPI_Direction_1Line_Tx |
		SPI_BaudRatePrescaler_2;

	// enable SPI port
	SPI1->CTLR1 |= CTLR1_SPE_Set;
	
	// always succeed
	return 0;
}

/*
 * toggle reset line
 */
void ssd1306_rst(void)
{
	SSD1306_RST_LOW();
	Delay_Ms(10);
	SSD1306_RST_HIGH();
}

/*
 * packet send for blocking polled operation via spi
 */
uint8_t ssd1306_pkt_send(uint8_t *data, uint8_t sz, uint8_t cmd)
{
	if(cmd)
		SSD1306_DC_LOW();
	else
		SSD1306_DC_HIGH();
	SSD1306_CS_LOW();
	
	// send data
	while(sz--)
	{
		// wait for TXE
		while(!(SPI1->STATR & SPI_STATR_TXE));
		
		// Send byte
		SPI1->DATAR = *data++;
	}
	
	// wait for not busy before exiting
	while(SPI1->STATR & SPI_STATR_BSY);
	
	SSD1306_CS_HIGH();
	
	// we're happy
	return 0;
}

#endif

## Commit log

2024-07-28 add KiCad files
    [FreqCounter3203-2024-07-25-21-31-20.sch, FreqCounter3203.kicad_pcb, FreqCounter3203.kicad_sch, FreqCounter3203.sch]
2024-07-30 add sample source
2024-07-30 change kicad files
    [FreqCounter3203-BOM.xlsx, FreqCounter3203-B_Cu.gbr, FreqCounter3203-B_Mask.gbr, FreqCounter3203-B_Silkscreen.gbr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]
2024-08-01 change MIC module OUT pin assign
2024-08-05 support micros() and millis() by SysTick
2024-08-10 imprement LED flash feature in tone mode
